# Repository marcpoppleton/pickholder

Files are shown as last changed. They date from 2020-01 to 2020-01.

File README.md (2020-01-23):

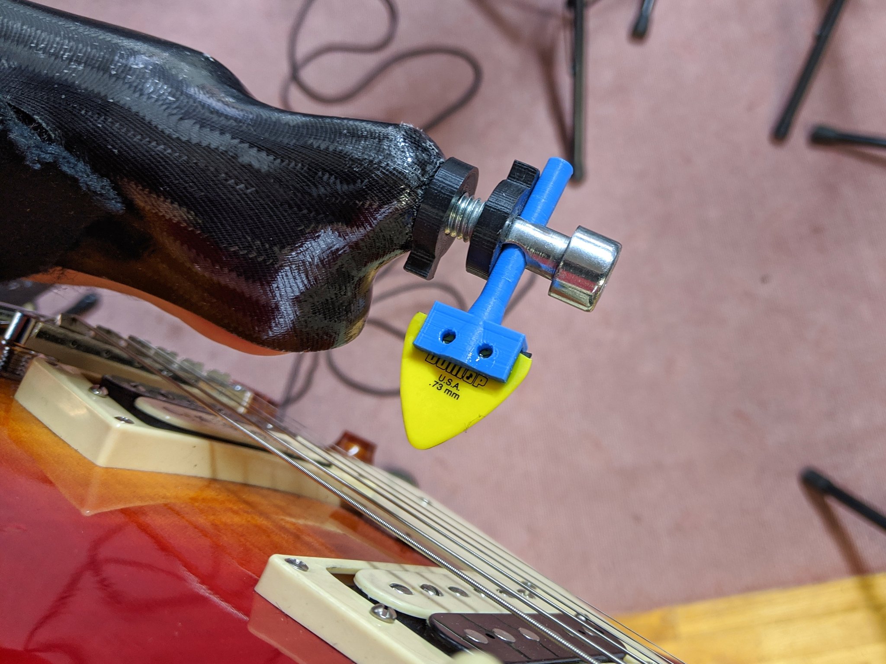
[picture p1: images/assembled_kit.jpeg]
Image of Assembled device


# Overview

This project is not meant to be a universal solution to all hand-lacking wannabe guitarists, it just fits my handicap. I'm sharing it so that anyone having the same kind of disability as mine, no hand with a short stump after the elbow, can give it a try. I'm also sharing it so that any fellow maker can contribute by providing improvements and alternative takes.

# Building it

* [Requirements](#Requirements)
* [Parts](#Parts)
* [Printing](#Printing)
* [Assembling](#Assembling)

## Requirements

* a missing hand (left or right, you choose)
* access to a 3D printer
* a guitar
* guitar picks

## Parts

The build is composed of several parts. The parts are:

* The socket element
* The mounting screw
* Two tightening bolts
* The pick holder
* The almighty pick of destiny

### Socket element

This part is not included in the project. It should be made by a prosthetist to fit properly the stump and prevent injuries. On mine the inner side is opened to allow me to mute the strings with the skin of my stump.
To allow the mounting screw to be held to the socket a M10 captive bolt is embedded in the socket.

### Mounting screw

The mounting screw used in this project is a CHC 10 stainless steel screw, typically used to fix climbing holds to walls. A 7mm unthreaded hole is drilled across the unthreaded part of the screw, just above the limit of the threading.
The mounting screw is to be screwed to the captive bolt held in the socket, a tightening bolt locking it in its desired position.

### Tightening bolts

Two different tightening bolts are used in the project:

* short\_tightening\_bolt.scad
* tightening_bolt.scad

#### Short tightening bolt

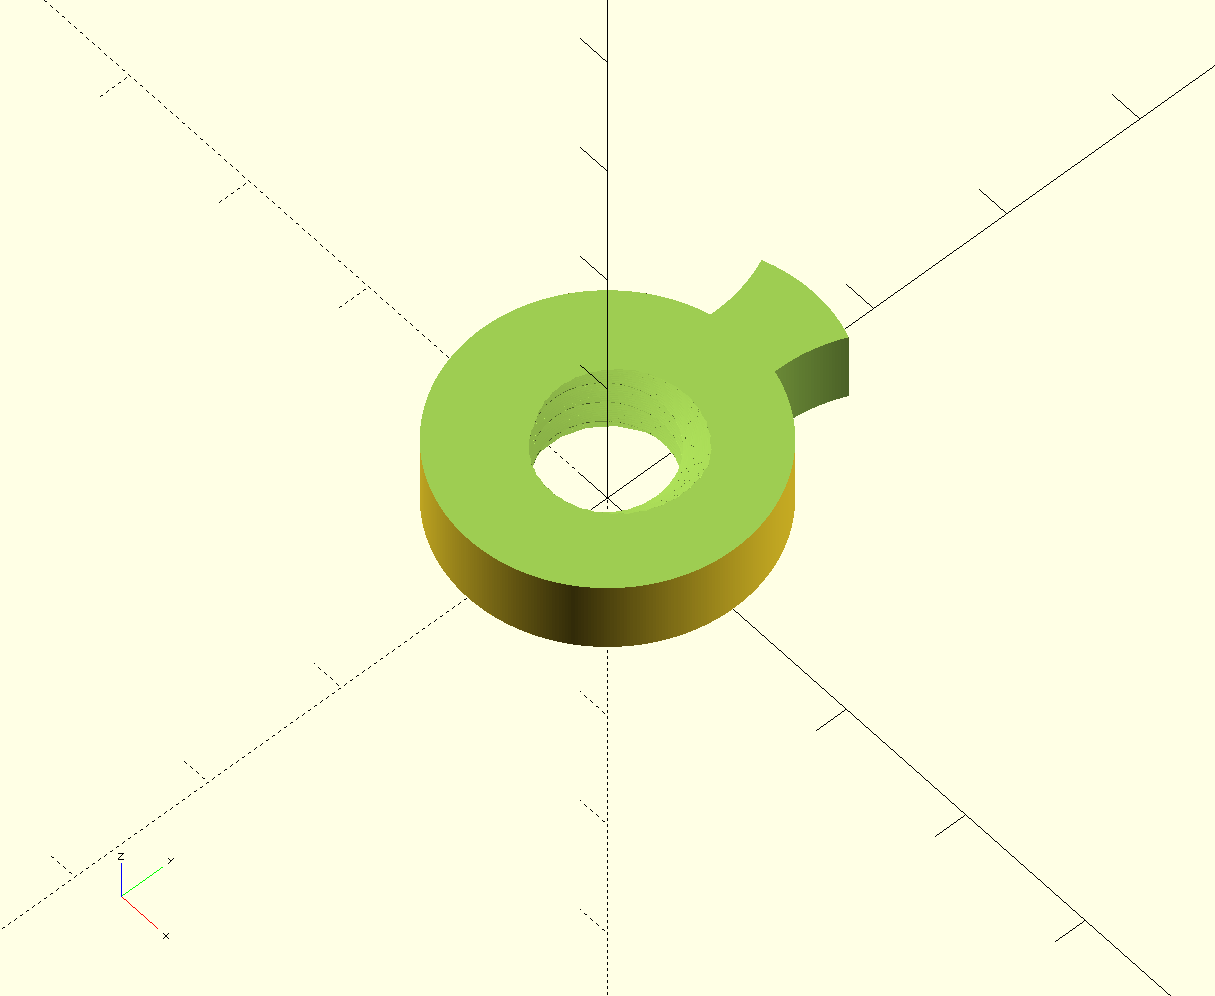
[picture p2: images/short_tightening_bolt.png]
Image of short tightening bolt


This bolt is intended to fix the mounting screw in position.

#### Tightening bolt

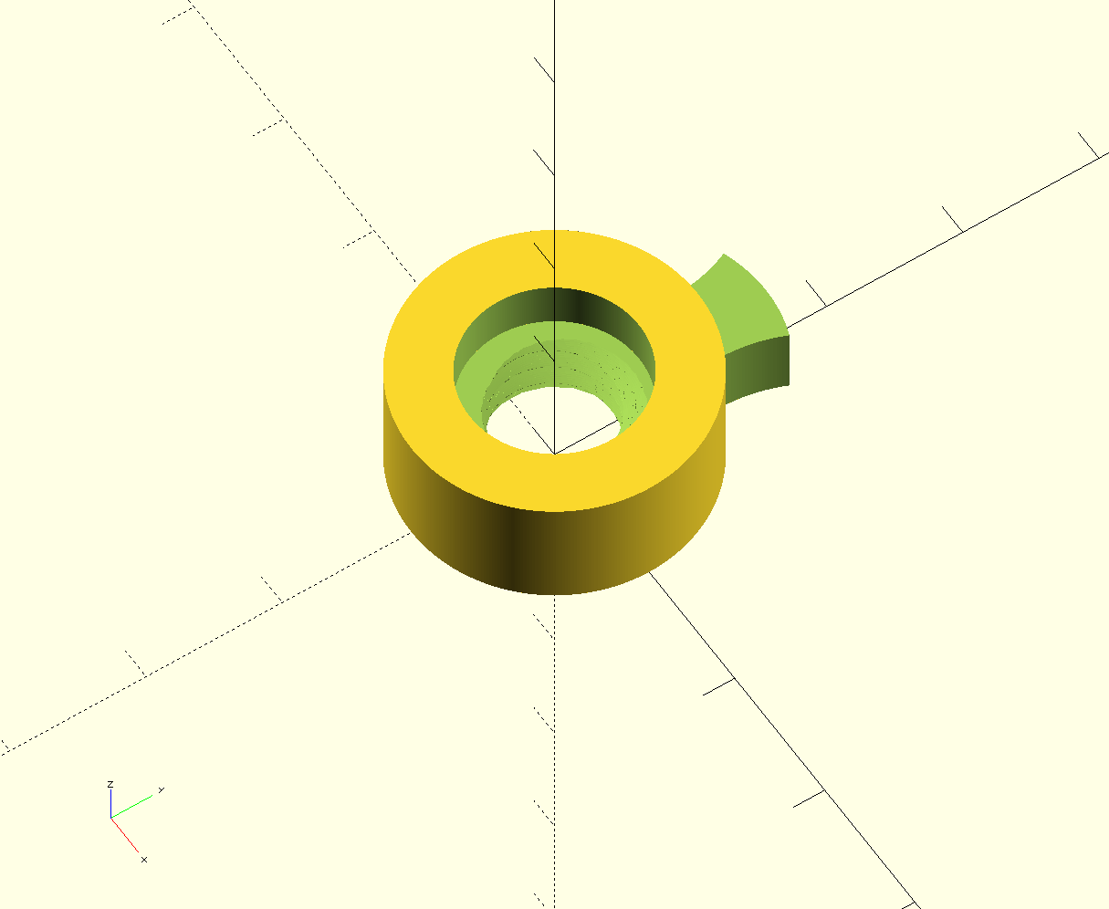
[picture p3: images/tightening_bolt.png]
Image of short tightening bolt


This bolt is intended to fix the pick holder within the mounting screw. The unthreaded part is ment to apply pressure against the shaft of the pick holder.

### Pick holder

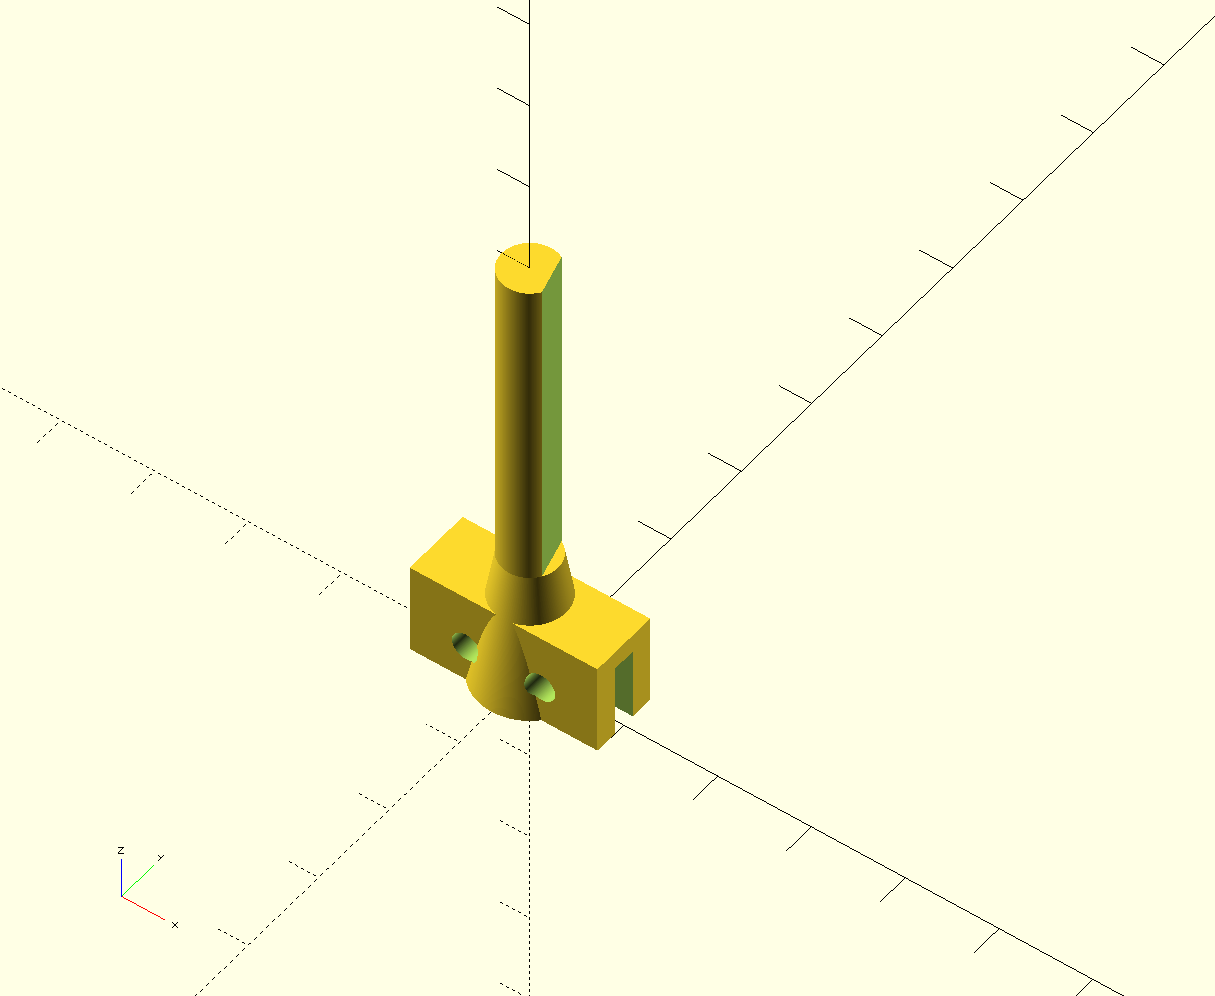
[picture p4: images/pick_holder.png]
Image of pick holder

 
This is the main part of the project. It is meant to hold the pick in the slot at the bottom. The flat surface on the shaft should be in front of the tightening bolt in order to provide a secure and tight locking. According to the shape of the stump, the angle of the flat surface must be adapted. See Printing section for details.  

### The almighty pick of destiny

Sadly we cannot show you pictures of aforementioned Pick Of Destiny since it has been reclaimed by the Devil. Tenacious D is currently on the case.

## Printing

The tightening bolts and the pick holder STL files are provided in the [STL](https://github.com/marcpoppleton/pickholder/tree/master/stl) folder of the repository and can be used to print the parts on a 3D printer.

### Adjusting

The SCAD files are provided in the repository in the [SCAD](https://github.com/marcpoppleton/pickholder/tree/master/scad) folder. The bolt files require the [NutsnBolts OpenSCAD library](https://github.com/JohK/nutsnbolts).

## Assembling

### Step 1

The first step of the assembling stage is to prepare the picks.

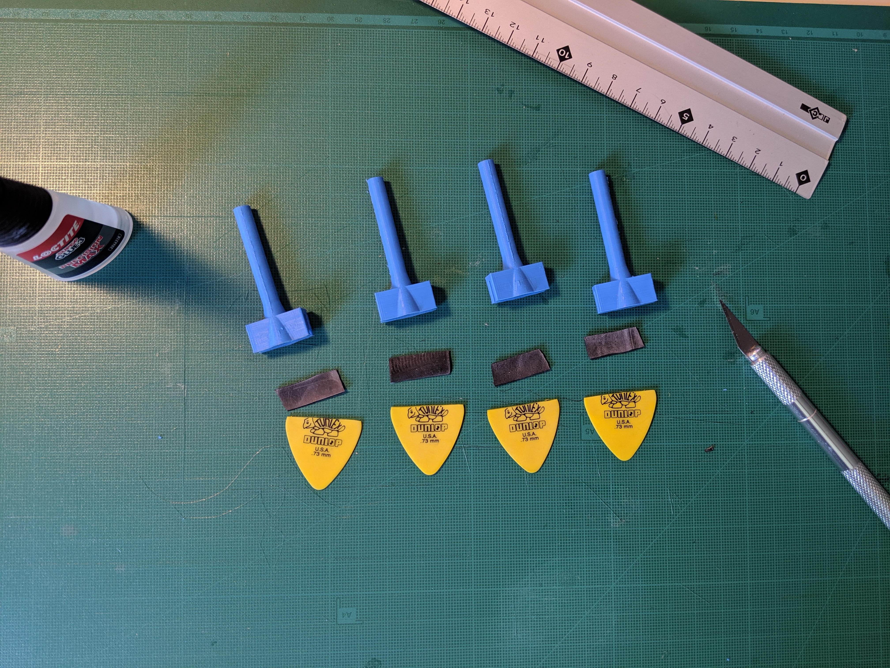
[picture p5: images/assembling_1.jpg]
Image of picks


The larger side of the pick must be cut with a cutting tool in order to give it a straight edge that will be pushed inside the slot of the pick holder.

### Step 2

The second step is to put it all together

Image of picks
 
The part inserted in the pick holder can be padded with rubber (collected from an old bicycle air chamber for example). CA glue is used to fix the pick to the pick holder.

### Step 3

Insert the pick holder in the mounting screw, secure the tightening bolt, and play!

## Author

Marc Poppleton, marc.poppleton@gmail.com

## Contributing

I would love you to contribute to **pickholder**, check the [CONTRIBUTING](https://github.com/marcpoppleton/pickholder/blob/master/CONTRIBUTING.md) file for more info.

## License

**pickholder** is available under the Apache 2.0. See the [LICENSE](https://github.com/marcpoppleton/pickholder/blob/master/LICENSE) file for more info.

## Special Thanks
Special thanks to [Orthofiga](http://www.orthofiga.com/) for the custom socket and all the musicians or makers who have help me designing this tool.

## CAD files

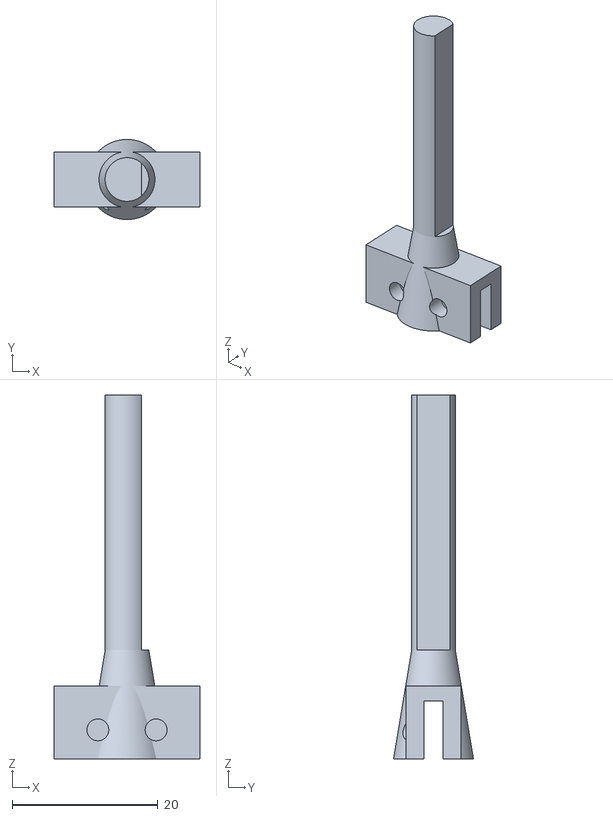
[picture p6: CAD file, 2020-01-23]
stl/pick_holder_no_angle.stl
20.0 x 11.0 x 50.0

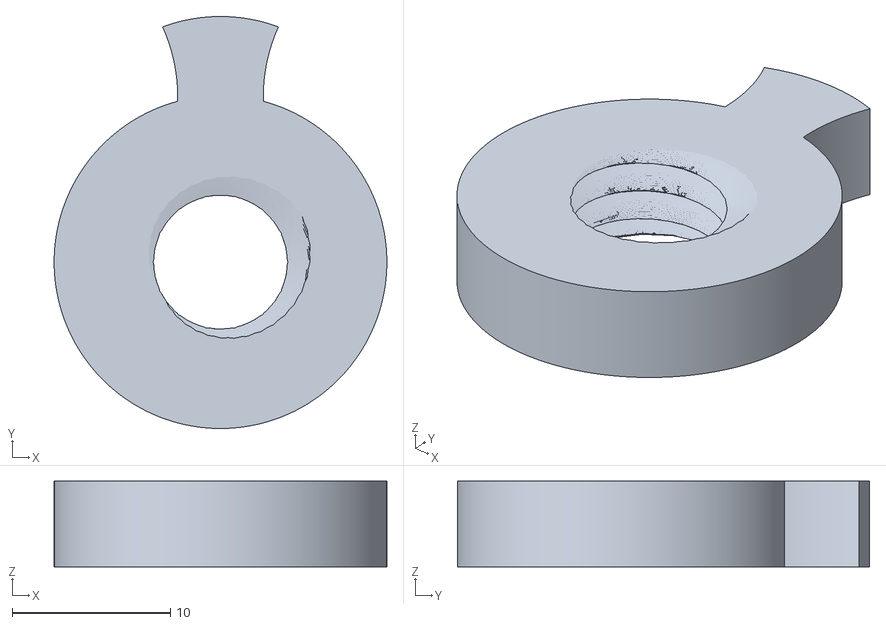
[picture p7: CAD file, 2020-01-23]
stl/short_tightening_bolt.stl
21.0 x 26.0 x 5.40

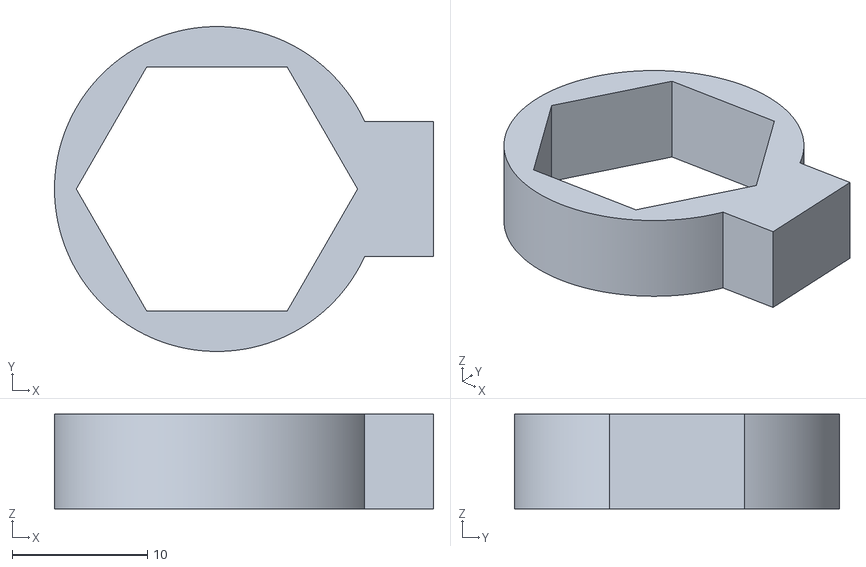
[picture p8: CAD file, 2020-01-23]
stl/tightening_bolt.stl
28.0 x 24.0 x 7.00

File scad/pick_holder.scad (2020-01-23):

//!OpenSCAD
include <nutsnbolts/cyl_head_bolt.scad>;

flat_angle = 15;

difference() {
  //Begining of main structure  
  difference() {
    union(){
        difference(){
          //main shaft
          cylinder(r1=3, r2=3, h=50, $fn=360,center=false);
          //flat spot
          rotate([0,0,flat_angle]){
          translate([5,0,50]){
            cube([6,6,75],center=true);
          }
        }
      }         

      cylinder(r1=5.5, r2=3, h=15, $fn=360,center=false);
      translate([0, 0, 5]){
        cube([20, 7.5, 10], center=true);
      }
    }
    

    //Slit for pick
    translate([0, 0, 4]){
      cube([20, 2.6, 8], center=true);
    }
    //End of slit
  }
  //End of main structure

  //Begining of drill holes
  union(){
     translate([-4, 3, 4]){
      rotate([90, 0, 0]){
          cylinder(r1=1.5, r2=1.5, h=8, $fn=360,center=false);
      }
    }
     translate([4, 3, 4]){
      rotate([90, 0, 0]){
          cylinder(r1=1.5, r2=1.5, h=8, $fn=360,center=false);
      }
    }
  }
  //End of drill holes
}

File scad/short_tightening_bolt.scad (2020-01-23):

//!OpenSCAD
include <nutsnbolts/cyl_head_bolt.scad>;

type = "M12";

	df = _get_fam(type);
	nutkey = df[_NB_F_NUT_KEY];
	nutheight = df[_NB_F_NUT_HEIGHT];
	orad = df[_NB_F_OUTER_DIA]/2;
	lead = df[_NB_F_LEAD];
	irad = orad-lead;
    

difference(){

union(){
    translate([0,0,nutheight]){
        nut(type, thread="modeled");
    }
    //Round body around nut
    difference(){
        cylinder(r1=(nutkey/2)+1.5, r2=(nutkey/2)+1.5, h=nutheight,$fn=360, center=false);
        translate([0,0,-1]){
            cylinder(r1=orad, r2=orad, h=nutheight+2,$fn=360, center=false);
        }
    }
    //End of round body

    //Knob
    translate([0,5,0]){
    difference() {
      cylinder(r1=(nutkey/2)+1.5, r2=(nutkey/2)+1.5, h=nutheight,$fn=360, center=false);
    
      union(){
        translate([1.25*nutheight, nutheight/2, 0]){
          cylinder(r1=nutheight, r2=nutheight, h=nutheight,$fn=360, center=false);
        }
        translate([-(1.25 * nutheight), nutheight/2, 0]){
          cylinder(r1=nutheight, r2=nutheight, h=nutheight,$fn=360, center=false);
        }
        translate([-nutheight/2, -0.75*nutkey, 0]){
          cube([nutkey, nutkey, nutheight], center=false);
        }
      }
    }    
    }
    //End of knob
}
//Slices the nut in two
translate([-nutkey,-nutkey,nutheight/2]){
          cube([nutkey*2, nutkey*2, nutheight], center=false);    
}
//End of slicing the nut in two
}

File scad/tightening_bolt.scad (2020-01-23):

//!OpenSCAD
include <nutsnbolts/cyl_head_bolt.scad>;

type = "M12";

	df = _get_fam(type);
	nutkey = df[_NB_F_NUT_KEY];
	nutheight = df[_NB_F_NUT_HEIGHT];
	orad = df[_NB_F_OUTER_DIA]/2;
	lead = df[_NB_F_LEAD];
	irad = orad-lead;
    

union(){
    //Round body pressing pick holder
    translate([0,0,nutheight/2]){
    difference(){
        cylinder(r1=(nutkey/2)+1.5, r2=(nutkey/2)+1.5, h=nutheight/3,$fn=360, center=false);
        translate([0,0,-1]){
            cylinder(r1=orad+0.2, r2=orad+0.2, h=nutheight+2,$fn=360, center=false);
        }
    }
}
    //End of body pressing pixk holder


difference(){

union(){
    translate([0,0,nutheight]){
        nut(type, thread="modeled");
    }
    //Round body around nut
    difference(){
        cylinder(r1=(nutkey/2)+1.5, r2=(nutkey/2)+1.5, h=nutheight,$fn=360, center=false);
        translate([0,0,-1]){
            cylinder(r1=orad, r2=orad, h=nutheight+2,$fn=360, center=false);
        }
    }
    //End of round body

    //Knob
    translate([0,5,0]){
    difference() {
      cylinder(r1=(nutkey/2)+1.5, r2=(nutkey/2)+1.5, h=nutheight,$fn=360, center=false);
    
      union(){
        translate([1.25*nutheight, nutheight/2, 0]){
          cylinder(r1=nutheight, r2=nutheight, h=nutheight,$fn=360, center=false);
        }
        translate([-(1.25 * nutheight), nutheight/2, 0]){
          cylinder(r1=nutheight, r2=nutheight, h=nutheight,$fn=360, center=false);
        }
        translate([-nutheight/2, -0.75*nutkey, 0]){
          cube([nutkey, nutkey, nutheight], center=false);
        }
      }
    }    
    }
    //End of knob
}
//Slices the nut in two
translate([-nutkey,-nutkey,nutheight/2]){
          cube([nutkey*2, nutkey*2, nutheight], center=false);    
}
//End of slicing the nut in two
}
}

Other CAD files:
stl/pick_holder_45_angle.stl
stl/pick_holder_10_angle.stl
stl/pick_holder_25_angle.stl
stl/pick_holder_35_angle.stl
stl/pick_holder_15_angle.stl
